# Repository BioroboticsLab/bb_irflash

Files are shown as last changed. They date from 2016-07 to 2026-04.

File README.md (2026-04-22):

# bb_irflash - Infrared LED flashing software and hardware

----
## What is bb_irflash?

bb_irflash is a software and hardware layout package. It contains the circuit and board layout for creating infrared flashing devices.

## Software

The software is C code written and tested for the Arduino Board Duemilanove. However, it should be easily adjusted to fit any arduino available on the market.

## Hardware

The hardware is designed to be triggered via signal current and powered with 12V. The design contains no protection mechanism whatsoever. So exchanging the resistors and/or LED's enables faster/slower flashing or constant lighting. 

The board dimensions are 23mmx51mm, single sided layout. Parts as described in the 'Parts' section enable flashing at 3 Hz and 20 ms duration. Designs come in EAGLE format.

# Parts

## SMD Parts Required for the Boards

The following Surface-Mount Device (SMD) parts are required for the boards:

### MOSFETs
- 8x [NTMS4807NR2G 'AO4752'](https://www.mouser.de/ProductDetail/863-NTMS4807NR2G)

### LEDs
- 8x [LED OSRAM 'SFH 4716AS A01'](https://www.mouser.de/ProductDetail/ams-OSRAM/SFH-4716AS-A01?qs=%252BEew9%252B0nqrDXvNyoSKrong%3D%3D)

### Signal Amplifiers
- 4x [Signal Amplifier 'LM358LVIDR'](https://www.mouser.de/ProductDetail/595-LM358LVIDR)

### Resistors
- 32x [2 Ohm Resistor '603-RC2512JK-072RL'](https://www.mouser.de/ProductDetail/603-RC2512JK-072RL)
- 16x [10k Ohm Resistor '71-CRCW060310K0JNEAC'](https://www.mouser.de/ProductDetail/71-CRCW060310K0JNEAC)
- 2x [4.7k Ohm Resistor '71-CRCW06034K70JNEAC'](https://www.mouser.de/ProductDetail/71-CRCW06034K70JNEAC)
- 4x [22k Ohm Resistor '71-CRCW060322K0JNEAC'](https://www.mouser.de/ProductDetail/71-CRCW060322K0JNEAC)
- 1x [20k Ohm Resistor 'R0603'](Beta Layout standard part) [20k Resistor on Mouser '71-CRCW060320K0JNEA'](https://www.mouser.de/ProductDetail/71-CRCW060320K0JNEAC)
)
- 1x [100k Ohm Resistor '71-CRCW0603100KFKEAC'](https://www.mouser.de/ProductDetail/71-CRCW0603100KFKEAC)

### Capacitors
- 4x [0.01uF Capacitor '810-C1005X7R1H103KBE'](https://www.mouser.de/ProductDetail/810-C1005X7R1H103KBE)
- 2x [1uF Capacitor '81-GRM155R61C105MA2D'](https://www.mouser.de/ProductDetail/81-GRM155R61C105MA2D)

### Diodes
- 2x [Schottky Diode 'CDBU0230R-HF'](https://www.mouser.de/ProductDetail/750-CDBU0230R-HF)

### Transistors
- 2x [NPN Transistor 'NSVMMBT2222AM3T5G'](https://www.mouser.de/ProductDetail/863-NSVMMBT2222AM3T5)

### Timer
- 2x [Timer 'NE555DR'](https://www.mouser.de/ProductDetail/595-NE555DR)

### Logic Gates
- 1x [Dual AND Gate '74LVC2G08'](https://www.mouser.de/ProductDetail/771-74LVC2G08DP-G)

## Through-hole-technology (THT) required components to solder on

### Capacitors
- 8x [2mF Capacitor '667-EEU-FP1E202B'](https://www.mouser.de/ProductDetail/667-EEU-FP1E202B)

### MOSFET
- 1x [STD12NF06L-1 'STD12NF06L-1'](https://www.mouser.de/ProductDetail/511-STD12NF06L-1)

### Connectors
- 8x [Header - Board to LED connections](https://www.mouser.de/ProductDetail/538-43045-0400)
- 1x [Header - Arduino connection](https://www.mouser.de/ProductDetail/538-105313-1203).  Note that the picture shows the incorrect part with number 1103.  The right angle connection
- 1x [Header - Power supply connection](https://www.mouser.de/ProductDetail/538-76825-0002)

See order_examples for further detail, and reference the picture for needed parts.  

# Mouser project order templates for parts:
- [bb_irflash SMD components Mouser project to order](https://eu.mouser.com/ProjectManager/ProjectDetail.aspx?AccessID=517e59b65d)
- [bb_irflash SMD components spreadsheet list](order_examples/BB_IRFLASH_SMD_COMPONENTS.xls)
- [bb_irflash THT components Mouser project to order](https://eu.mouser.com/ProjectManager/ProjectDetail.aspx?AccessID=0B309C354D)
- [bb_irflash THT components spreadsheet list](order_examples/BB_IRFLASH_THT_COMPONENTS.xls)
- [Cables for connecting lights, Arduino, and power supply](https://www.mouser.de/ProjectManager/ProjectDetail.aspx?AccessID=e691302b18). Note that the Arduino connection cable (Nanofit) and the power supply cable (Megafit) connect to the board, but will have to be cut/adjusted to make appropriate connections to the Arduino/power supply

# Power supply
The board is typically driven at 5V.  However, higher light output can be achieved by driving at slightly higher voltages.  here are suitable power supply for these voltages.  Note that when operating at 6fps and 5msec flashes, one board will draw 1-1.5 amps maximum.  Therefore one of these power supplies is sufficient to drive multiple boards.
- [5V power supply (adjustable in range 4.75-5.8V)](https://www.mouser.de/ProductDetail/MEAN-WELL/HRP-100-5?qs=Pc4kzEvJlcQLHIPhYtoJzw%3D%3D)
- [7.5V power supply (adjustable in range 6-9V)](https://www.mouser.de/ProductDetail/MEAN-WELL/RSP-320-7.5?qs=Uzd%2Fwh%252BZzhAvdwoq1II01Q%3D%3D).  Also available at [Conrad](https://www.conrad.de/de/p/mean-well-rsp-320-7-5-schaltnetzteil-7-5-v-dc-40-a-300-w-2249344.html?utm_source=google&utm_medium=cpc&utm_campaign=GB1_Messtechnik+%26+Stromversorgung_Generic&utm_id=43483581&gad_source=1&gbraid=0AAAAAD1-3H5RXiWIoMa0wxSd_K8oRlJKH&gclid=CjwKCAiAudG5BhAREiwAWMlSjDPmVMJK24BTLvHd9yjfUtIwc8q5r0EybappmSUyCZYAYHu7tNM5choC1wwQAvD_BwE&refresh=true)

# Board V2.0

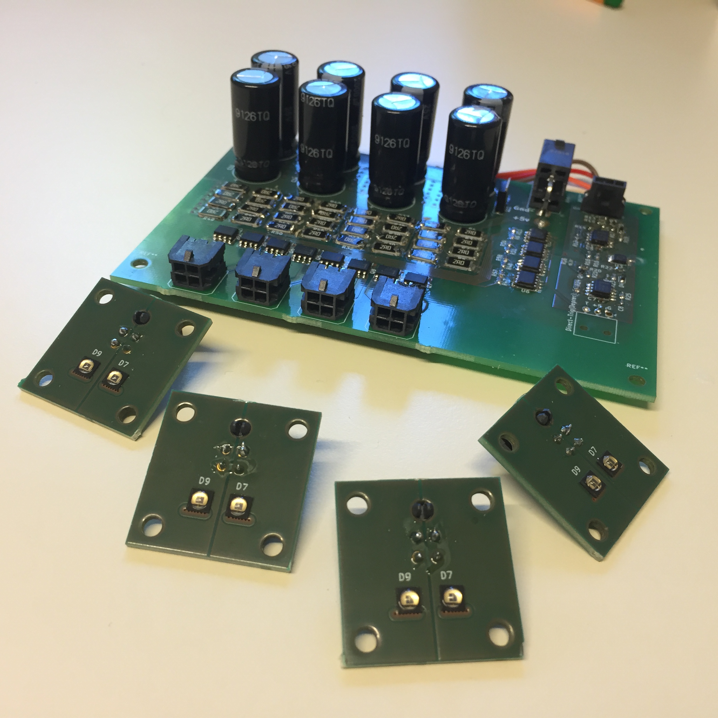
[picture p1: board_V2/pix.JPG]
BoardV2


The new IR flash board have the exact same performance as the previous version. The only new part is a better connectivity and a protection circuit.
The protection circuit is limiting the impulse duration to 20ms with a pause of 100ms between each pulse for protecting the LED. The power supply should be 
V ; 6A. To use it just send a step signal of the wanted duration to the trigger pin of the board (The step signal should not be wider than 20ms high and a pause of 100ms should be observe between each pulse)

The files in "board_V2" folder are all the project file in KiCAD format. If you have no interest in redesign, they are not interesting for you. 

For fabrication you only need the files in the fabrication folder.
The gerber files contained in "fabrication/gerber" are the map of your circuits - You manufacturer would ask for them (likely as a zip file, i.e. gerber.zip containing all folder contents).  The subfolder : "fabrication/gerber/drill_file" contain the coordinate of all the holes drilled into the board.

If you want to ask a third party for assembly, you will need the gerber files, the components position files ("Bestückungsplan": assembly_map_top.pdf
and assembly_map_bottom.pdf), the Pick&Place placement file (Pick&Place.txt), and the components list (Bill of Materials: BOM.xlsx). The 
The components position files are in component_position folder (Bottom and top layer). Note that the BOM format can vary in function of your third party company.

The folder order_examples contains two examples for orders placed through Beta Layout with components ordered through Mouser.  These are for reference.

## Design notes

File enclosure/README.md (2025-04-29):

# Case for Board v2

**Dimensions**:
- Top: 127 x 90 x 31mm
- Bottom: 127 x 90 x 17mm

**Material used:** Black PLA
**Nozzle Size:** 0.4 mm

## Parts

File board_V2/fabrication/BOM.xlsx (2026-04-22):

BILL OF MATERIALS | GROUPED BY VALUES | AS OF 03.14.2024
Part | Value | Device | Package | Description | Description2 | Qty | Place_YES/NO | Provided_by_customer_YES/NO | Distributor | ItemNumber | Remarks
C1, C6, C7, C4, | 0.01u | C | Capacitor_SMD:C_0402_1005Metric | Unpolarized capacitor | Multilayer Ceramic Capacitors MLCC - SMD/SMT SOFT 0402 50V 0.01uF X7R 10% T: 0.5mm | 4 | Y | N | Mouser | 810-C1005X7R1H103KBE | https://www.mouser.fr/ProductDetail/810-C1005X7R1H103KBE
C2, C3, C10, C9, C14, C12, C13, C11, | 2m | CP | Capacitor_THT:CP_Radial_D12.5mm_P5.00mm | Polarized capacitor | Aluminium Electrolytic Capacitors - Radial Leaded 25VDC 2000uF 20% ESR 0.030ohm | 8 | N | N | Mouser | 667-EEU-FP1E202B | https://www.mouser.fr/ProductDetail/667-EEU-FP1E202B
C5, C8, | 1u | C | Capacitor_SMD:C_0402_1005Metric | Unpolarized capacitor | Multilayer Ceramic Capacitors MLCC - SMD/SMT 0402 1uF 16volts X5R 20% | 2 | Y | N | Mouser | 81-GRM155R61C105MA2D | https://www.mouser.fr/ProductDetail/81-GRM155R61C105MA2D
D2, D1, D5, D6, D8, D10, D7, D9, | LED | LED | LED:SFH 4716AS A01 | Light emitting diode | Infrared Emitters - High Power Infrared 850 nm | 8 | Y | N | Mouser | 720-SFH4716ASAA5051 | https://www.mouser.de/ProductDetail/ams-OSRAM/SFH-4716AS-A01?qs=%252BEew9%252B0nqrDXvNyoSKrong%3D%3D
D3, D4, | CDBU0230R-HF | CDBU0230R-HF | Diode_SMD:D_0603_1608Metric | Diode | Schottky Diodes & Rectifiers VR=30V, IO=200mA | 2 | Y | N | Mouser | 750-CDBU0230R-HF | https://www.mouser.fr/ProductDetail/750-CDBU0230R-HF
Q2, Q1, Q5, Q6, Q8, Q10, Q7, Q9, | NTMS4807NR2G | AO4752 | Package_SO:SOIC-8_3.9x4.9mm_P1.27mm |  |  | 8 | Y | N | Mouser | 863-NTMS4807NR2G | https://www.mouser.fr/ProductDetail/863-NTMS4807NR2G
Q3, Q4, | NSVMMBT2222AM3T5G | Q_NPN_BCE | Package_TO_SOT_SMD:SOT-723 | NPN transistor, base/collector/emitter | Bipolar Transistors - BJT SS SOT-723 GP TRANSISTOR | 2 | Y | N | Mouser | 863-NSVMMBT2222AM3T5 | https://www.mouser.fr/ProductDetail/863-NSVMMBT2222AM3T5
Q11, | STD12NF06L-1 | STD12NF06L-1 | Package_TO_SOT_THT:TO-251-3_Vertical | 50V Vds, 0.22A Id, N-Channel MOSFET, SOT-23 | MOSFET TO-251AA N-Ch Power | 1 | N | N | Mouser | 511-STD12NF06L-1 | https://www.mouser.de/ProductDetail/511-STD12NF06L-1 (https://www.mouser.fr/ProductDetail/512-RFD14N05L)
R3, R4, R10, R9, R8, R2, R7, R5, R32, R27, R33, R34, R35, R30, R29, R28, R50, R40, R52, R54, R56, R46, R44, R42, R49, R39, R51, R53, R55, R45, R43, R41, | 2 | R | Resistor_SMD:R_2512_6332Metric | Resistor | Thick Film Resistors - SMD 2 OHM 5% | 32 | Y | N | Mouser | 603-RC2512JK-072RL | https://www.mouser.fr/ProductDetail/603-RC2512JK-072RL
R13, R12, R18, R16, R21, R22, R11, R6, R31, R36, R48, R58, R47, R57, R26, R1, | 10k | R | Resistor_SMD:R_0603_1608Metric | Resistor | Thick Film Resistors - SMD 1/10Watt 10Kohms 5% Commercial Use | 16 | Y | N | Mouser | 71-CRCW060310K0JNEAC | https://www.mouser.fr/ProductDetail/71-CRCW060310K0JNEAC
R15, R20, | 4.7k | R | Resistor_SMD:R_0603_1608Metric | Resistor | Thick Film Resistors - SMD 1/10Watt 4.7Kohms 5% Commercial Use | 2 | Y | N | Mouser | 71-CRCW06034K70JNEAC | https://www.mouser.fr/ProductDetail/71-CRCW06034K70JNEAC
R17, R14, R23, R24, | 22k | R | Resistor_SMD:R_0603_1608Metric | Resistor | Thick Film Resistors - SMD 1/10Watt 22Kohms 5% Commercial Use | 4 | Y | N | Mouser | 71-CRCW060322K0JNEAC | https://www.mouser.fr/ProductDetail/71-CRCW060322K0JNEAC
R19, | 20k | R0603 | Resistor_SMD:R_0603_1608Metric | Resistor |  | 1 | Y | N | Beta | R0603
R25, | 100k | R | Resistor_SMD:R_0603_1608Metric | Resistor | Thick Film Resistors - SMD 1/10Watt 100Kohms 1% Commercial Use | 1 | Y | N | Mouser | 71-CRCW0603100KFKEAC | https://www.mouser.fr/ProductDetail/71-CRCW0603100KFKEAC
U1, U5, U7, U6, | LMV358 | LMV358 | Package_SO:SOIC-8_3.9x4.9mm_P1.27mm | Dual Low-Voltage Rail-to-Rail Output Operational Amplifiers, SOIC-8/SSOP-8 | Operational Amplifiers - Op Amps Low Cost RRO amp General Purpose Dual | 4 | Y | N | Mouser | 595-LM358LVIDR | https://www.mouser.de/ProductDetail/Texas-Instruments/LM358LVIDR?qs=qSfuJ%252Bfl%2Fd53U%2FPkf9lZVw%3D%3D
U2, U4, | NE555DR | LM555 | Package_SO:SOIC-8_3.9x4.9mm_P1.27mm | Timer, DIP-8/SOIC-8/SSOP-8 | Timers & Support Products Precision | 2 | Y | N | Mouser | 595-NE555DR | https://www.mouser.fr/ProductDetail/595-NE555DR
U3, | 74LVC2G08 | 74LVC2G08 | Package_SO:TSSOP-8_3x3mm_P0.65mm | Dual AND Gate, Low-Voltage CMOS |  | 1 | Y | N | Mouser | 771-74LVC2G08DP-G | https://www.mouser.fr/ProductDetail/771-74LVC2G08DP-G

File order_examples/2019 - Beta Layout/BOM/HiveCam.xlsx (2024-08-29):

Source: | /media/huisse/Storage/Shared/HiveCamFinish/HiveCam.sch
Date: | Do 08 Aug 2019 11:50:28 CEST
Tool: | Eeschema 5.1.3-ffb9f22~84~ubuntu18.04.1
Generator: | /usr/share/kicad/plugins/bom_csv_grouped_by_value_with_fp.py
Component Count: | 98
Ref | Qnty | Value | Cmp name | Footprint | Description | Place_YES/NO | Povided_by_customer_YES/NO | Distributor | Remark
C1, C6, C7, C4, | 4 | 0.01u | C | Capacitor_SMD:C_0402_1005Metric | Unpolarized capacitor | Y | Y
C2, C3, C10, C9, C14, C12, C13, C11, | 8 | 2m | CP | Capacitor_THT:CP_Radial_D12.5mm_P5.00mm | Polarized capacitor | N | N |  | We will assemble them ourself
C5, C8, | 2 | 1u | C | Capacitor_SMD:C_0402_1005Metric | Unpolarized capacitor | Y | Y
D2, D1, D5, D6, D8, D10, D7, D9, | 8 | LED | LED | LED:SFH-4716S | Light emitting diode | Y | Y
D3, D4, | 2 | DIODE | DIODE | Diode_SMD:D_0603_1608Metric | Diode symbol for simulation only. Pin order incompatible with official kicad footprints | Y | Y
Q2, Q1, Q5, Q6, Q8, Q10, Q7, Q9, | 8 | NTMS4807NR2G | AO4752 | Package_SO:SOIC-8_3.9x4.9mm_P1.27mm |  | Y | Y
Q3, Q4, | 2 | NSVMMBT2222AM3T5G | Q_NPN_BCE | Package_TO_SOT_SMD:SOT-723 | NPN transistor, base/collector/emitter | Y | Y
Q11, | 1 | RFD14N05L | RFD14N05L | Package_TO_SOT_THT:TO-251-3_Vertical | 50V Vds, 0.22A Id, N-Channel MOSFET, SOT-23 | N | N
R3, R4, R10, R9, R8, R2, R7, R5, R32, R27, R33, R34, R35, R30, R29, R28, R50, R40, R52, R54, R56, R46, R44, R42, R49, R39, R51, R53, R55, R45, R43, R41, | 32 | 2 | R | Resistor_SMD:R_2512_6332Metric | Resistor | Y | Y
R13, R12, R18, R16, R21, R22, R11, R6, R31, R36, R48, R58, R47, R57, R26, R1, | 16 | 10k | R | Resistor_SMD:R_0603_1608Metric | Resistor | Y | Y
R15, R20, | 2 | 4.7k | R | Resistor_SMD:R_0603_1608Metric | Resistor | Y | Y
R17, R14, R23, R24, | 4 | 22k | R | Resistor_SMD:R_0603_1608Metric | Resistor | Y | Y
R19, | 1 | 20k | R | Resistor_SMD:R_0603_1608Metric | Resistor | Y | N | Beta | I saw you have this in stock
R25, | 1 | 100k | R | Resistor_SMD:R_0603_1608Metric | Resistor | Y | Y
U1, U5, U7, U6, | 4 | LMV358 | LMV358 | Package_SO:SOIC-8_3.9x4.9mm_P1.27mm | Dual Low-Voltage Rail-to-Rail Output Operational Amplifiers, SOIC-8/SSOP-8 | Y | Y
U2, U4, | 2 | NE555DR | LM555 | Package_SO:SOIC-8_3.9x4.9mm_P1.27mm | Timer, DIP-8/SOIC-8/SSOP-8 | Y | Y
U3, | 1 | 74LVC2G08 | 74LVC2G08 | Package_SO:TSSOP-8_3x3mm_P0.65mm | Dual AND Gate, Low-Voltage CMOS | Y | Y
Ref | Qnty | Value
C1, C6, C7, C4, | 35 | 0.01u
C2, C3, C10, C9, C14, C12, C13, C11, |  | 2m
C5, C8, | 56 | 1u
D2, D1, D5, D6, D8, D10, D7, D9, | 92 | LED
D3, D4, | 37 | DIODE
Q2, Q1, Q5, Q6, Q8, Q10, Q7, Q9, | 111 | NTMS4807NR2G
Q3, Q4, | 38 | NSVMMBT2222AM3T5G
Q11, |  | RFD14N05L
R3, R4, R10, R9, R8, R2, R7, R5, R32, R27, R33, R34, R35, R30, R29, R28, R50, R40, R52, R54, R56, R46, R44, R42, R49, R39, R51, R53, R55, R45, R43, R41, | 364 | 2
R13, R12, R18, R16, R21, R22, R11, R6, R31, R36, R48, R58, R47, R57, R26, R1, | 240 | 10k
R15, R20, | 35 | 4.7k
R17, R14, R23, R24, | 66 | 22k
R19, |  | 20k
R25, | 38 | 100k
U1, U5, U7, U6, | 56 | LMV358
U2, U4, | 38 | NE555DR
U3, | 19 | 74LVC2G08

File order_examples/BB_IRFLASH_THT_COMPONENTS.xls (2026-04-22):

BB_IRFLASH THT COMPONENTS
Mouser-Nr. | Herst.- Nr. | Hersteller | Kunden-Teilenr | Beschreibung | RoHS | Lebenszyklus | Stückzahl
538-105313-1203 | 105313-1203 | Molex | J2 | Sockel & Kabelgehäuse NanoFit RA Hdr TH SR 3Ckt 0.38UM Au Blk | RoHS-konform |  | 1
511-STD12NF06L-1 | STD12NF06L-1 | STMicroelectronics | Q11 | MOSFETs N-Ch 60V 12A | RoHS: Konform durch Ausnahmegenehmigung |  | 1
538-43045-0400 | 43045-0400 | Molex | J3, J4, J5, J6, J7, J8, J9, J10 | Sockel & Kabelgehäuse 4 CKT R/A HEADER | RoHS-konform |  | 8
538-76825-0002 | 76825-0002 | Molex | J1 | Sockel & Kabelgehäuse MegaFit Dual Row RA Header Tin 2Ckt | RoHS-konform |  | 1
667-EEU-FP1E202B | EEU-FP1E202B | Panasonic | C2, C3, C9, C10, C11, C12, C13, C14 | Aluminium-Elektrolyt-Kondensatoren - Radial bedrahtet 25VDC 2000uF 20% ESR 0.030ohm AECQ200 | RoHS-konform |  | 8

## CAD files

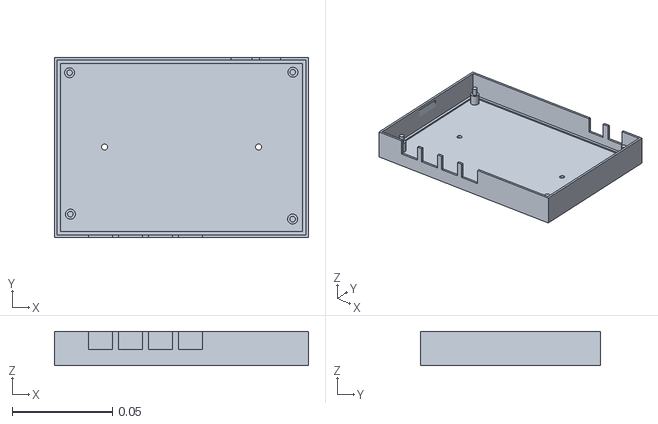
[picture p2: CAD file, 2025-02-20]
enclosure/enclosure_pcb_bottom_v2_20-02.2025.stl
0.127 x 0.09 x 0.017

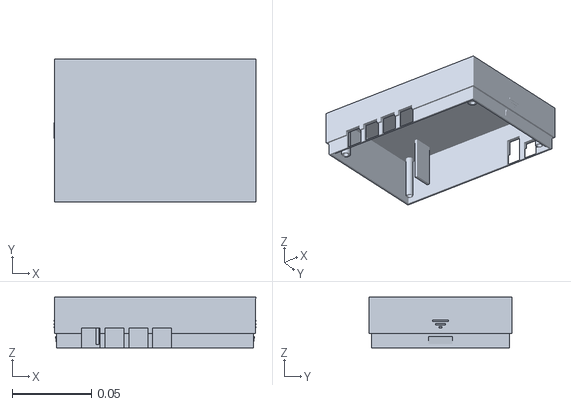
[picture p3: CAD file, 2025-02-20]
enclosure/enclosure_pcb_top_v2_20-02.2025.stl
0.127 x 0.09 x 0.032

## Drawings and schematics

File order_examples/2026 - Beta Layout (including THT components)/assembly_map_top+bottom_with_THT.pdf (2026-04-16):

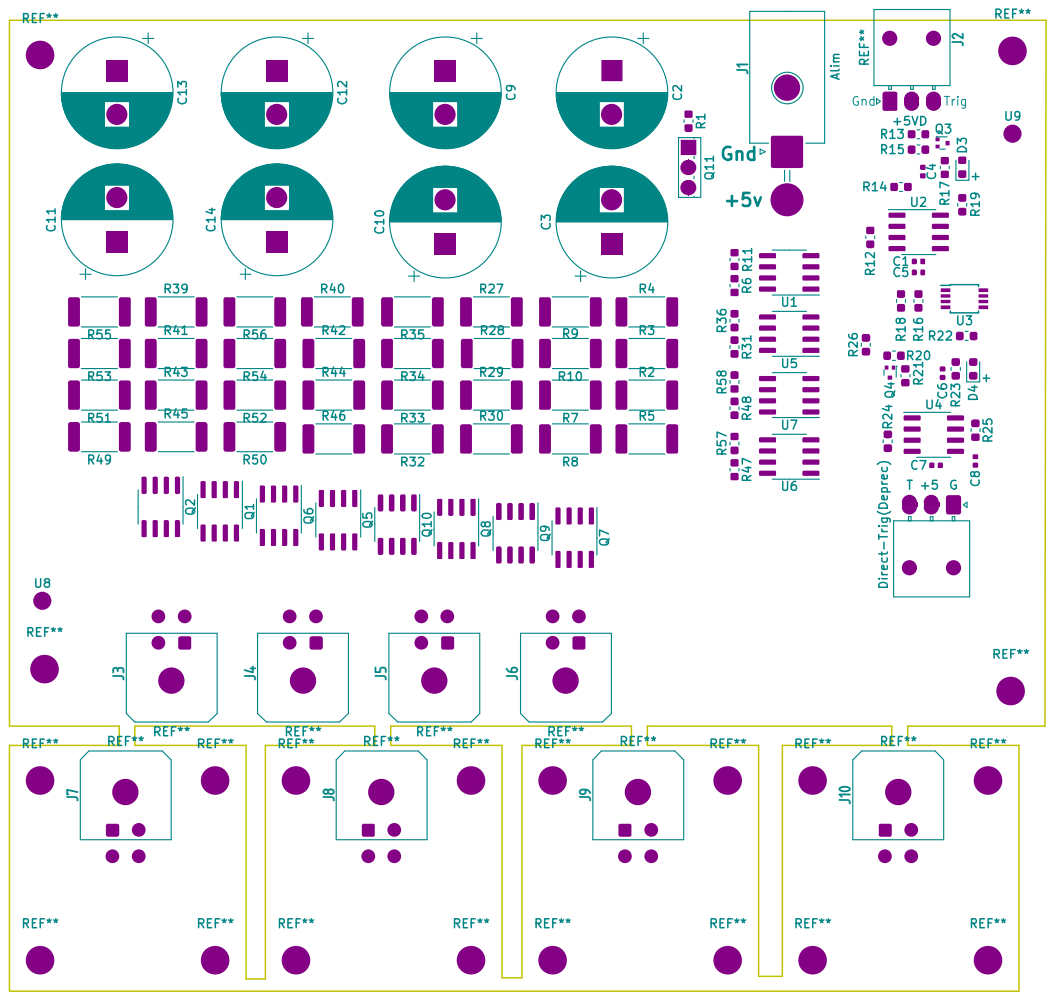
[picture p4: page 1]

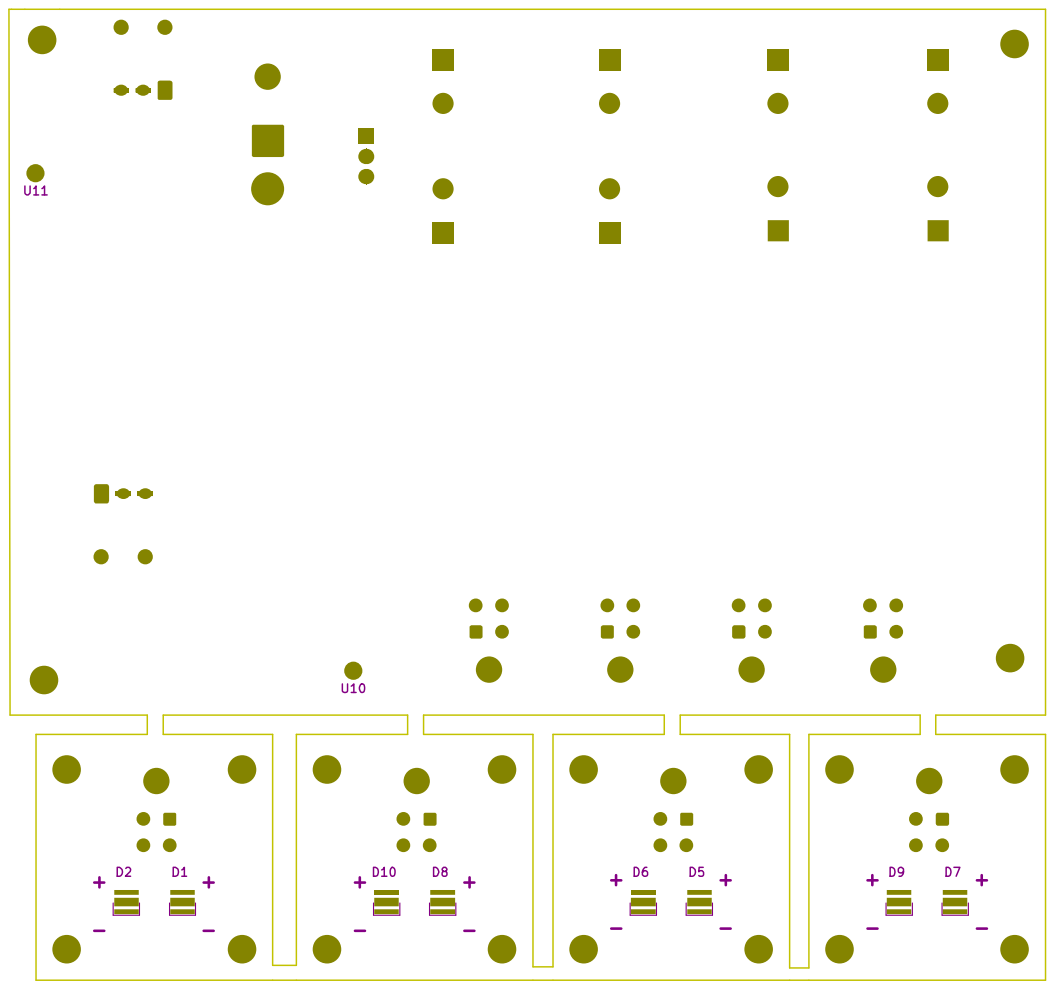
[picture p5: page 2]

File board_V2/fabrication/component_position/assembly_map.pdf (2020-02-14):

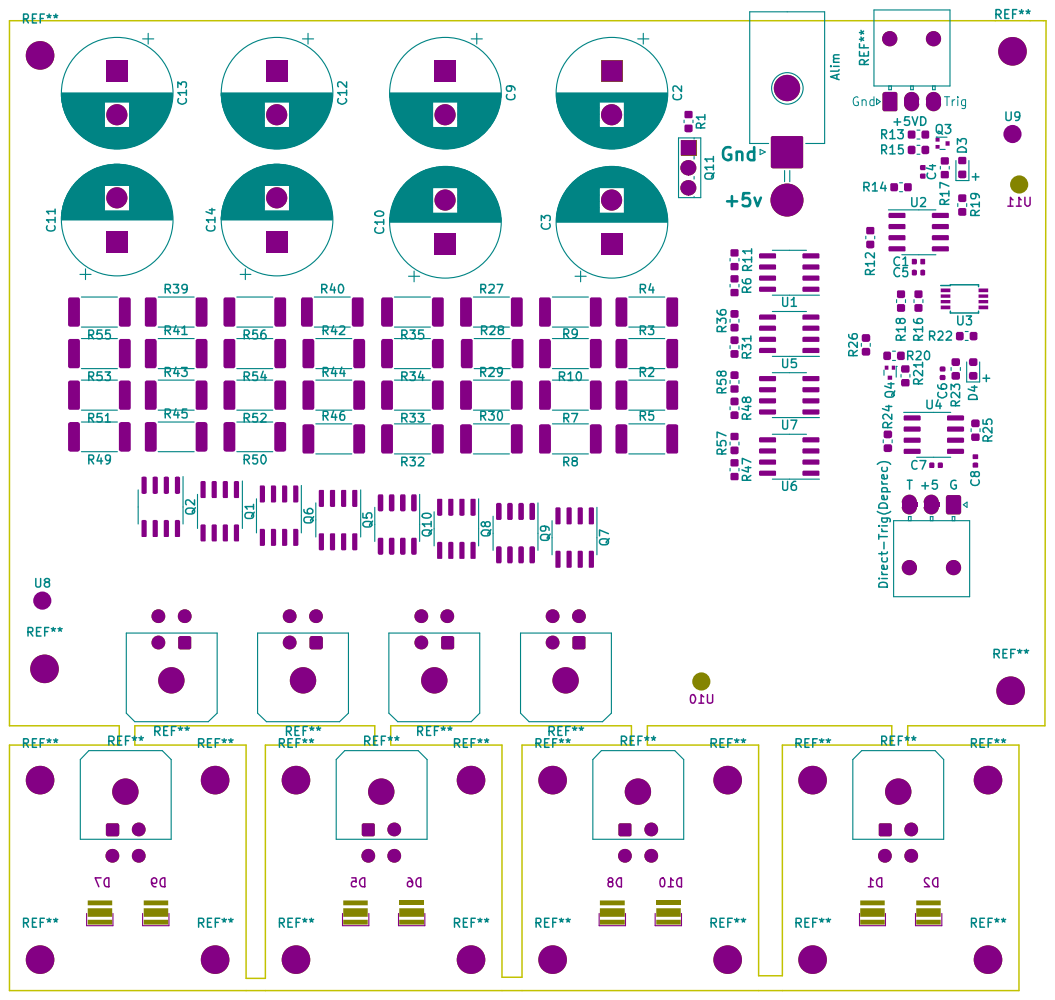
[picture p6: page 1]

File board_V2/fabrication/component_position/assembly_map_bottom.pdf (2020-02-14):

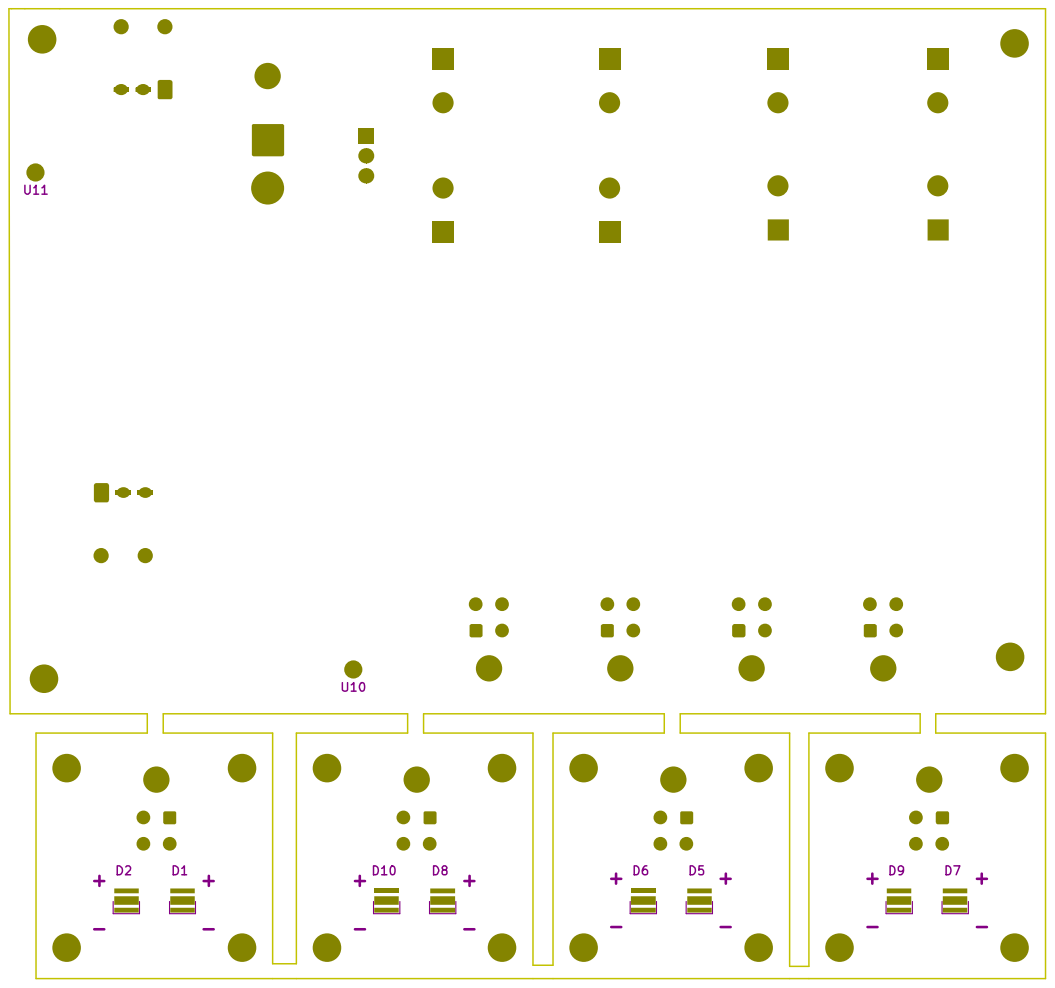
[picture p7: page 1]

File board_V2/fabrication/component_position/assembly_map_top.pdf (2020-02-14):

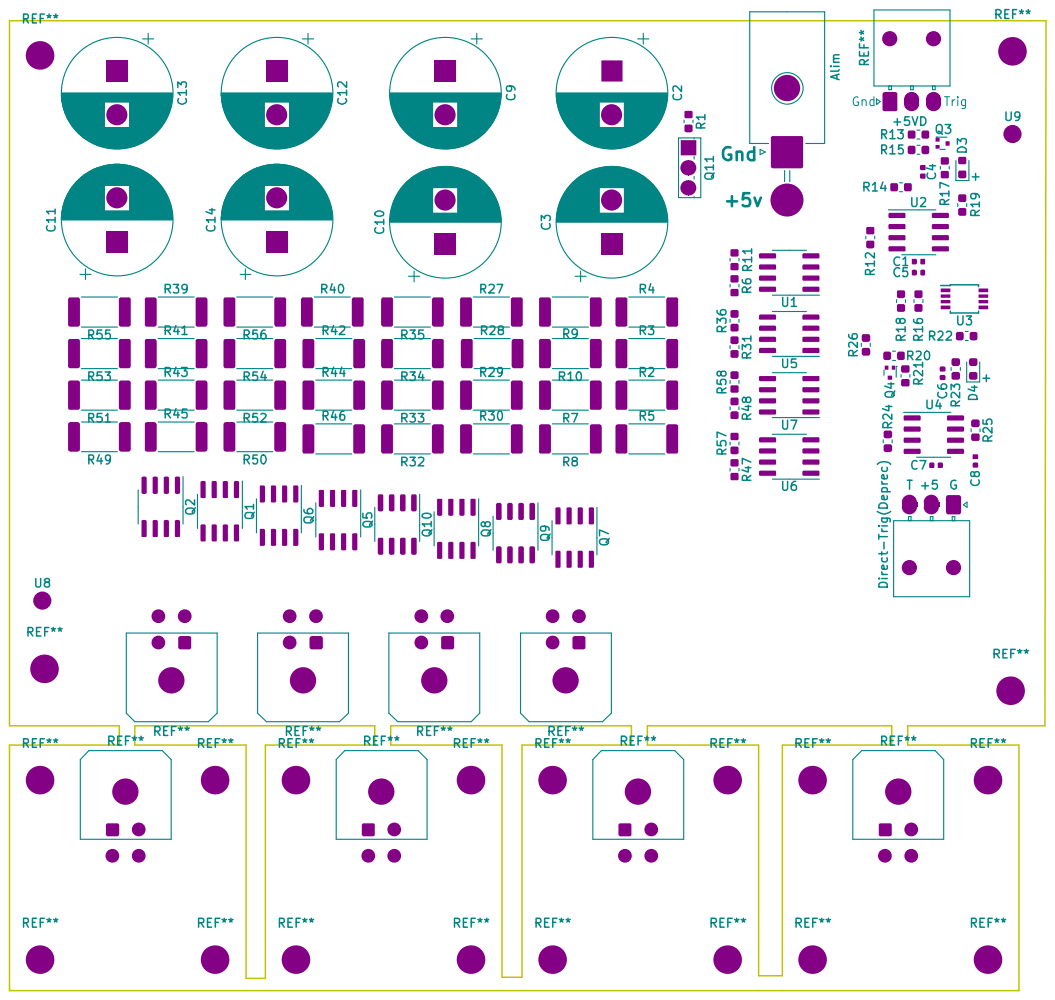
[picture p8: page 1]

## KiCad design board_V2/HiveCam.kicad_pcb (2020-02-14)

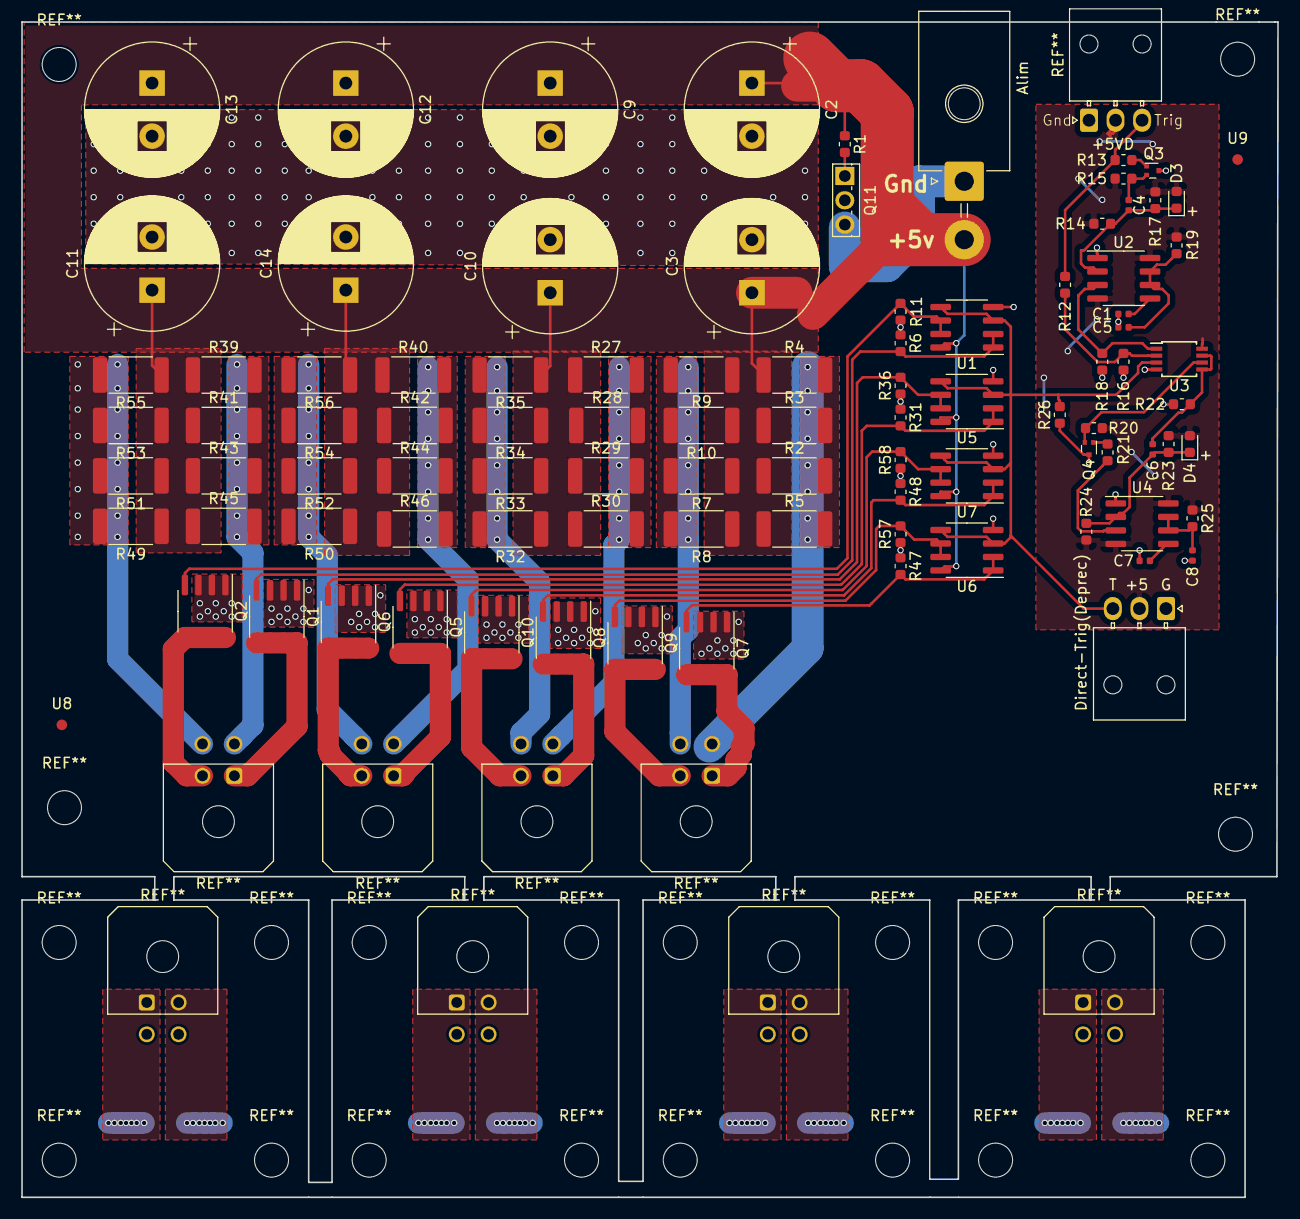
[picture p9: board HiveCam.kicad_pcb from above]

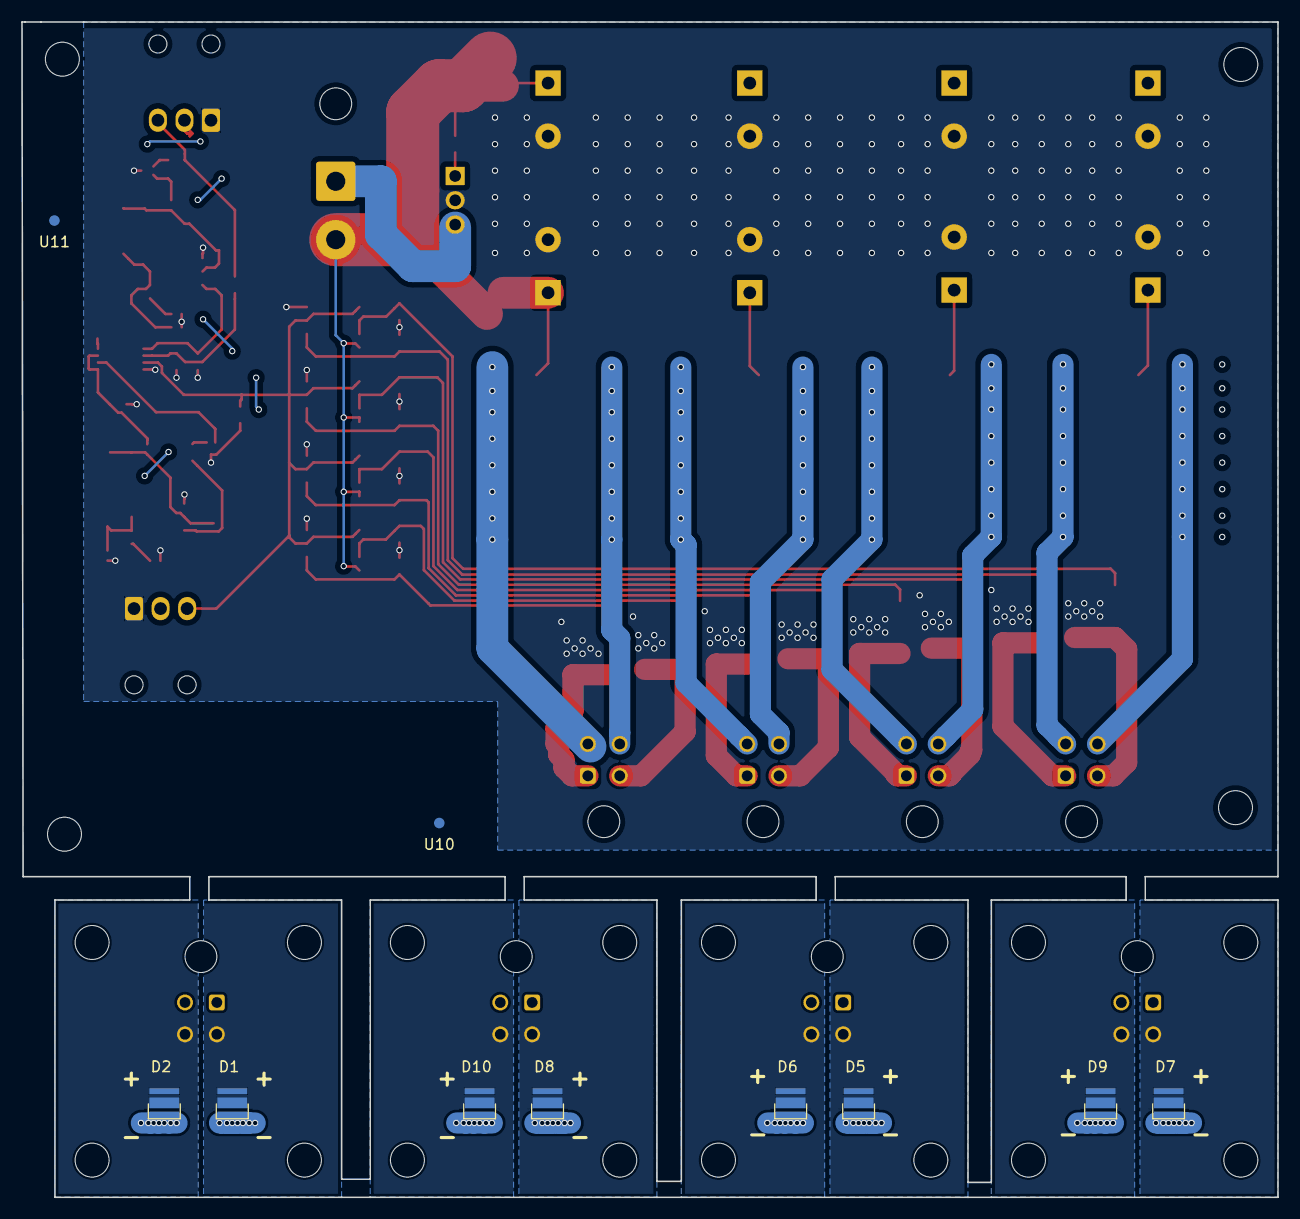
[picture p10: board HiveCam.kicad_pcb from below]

Board: 2 copper layers, 118.3 x 110.7 mm, 104 parts (10 on the bottom side), 39 nets.

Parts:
Alim: Molex_Mega-Fit_76825-0002_2x01_P5.70mm_Horizontal
C1, C4, C6, C7: 0.01u; C_0402_1005Metric
C2, C3, C9, C10, C11, C12, C13, C14: 2m; CP_Radial_D12.5mm_P5.00mm
C5, C8: 1u; C_0402_1005Metric
D1, D2, D5, D6, D7, D8, D9, D10: LED; SFH-4716S
D3, D4: DIODE; D_0603_1608Metric
Direct-Trig(Deprec): Molex_Nano-Fit_105313-xx03_1x03_P2.50mm_Horizontal
Q1, Q2, Q5, Q6, Q7, Q8, Q9, Q10: NTMS4807NR2G; SOIC-8_3.9x4.9mm_P1.27mm
Q3, Q4: NSVMMBT2222AM3T5G; SOT-723
Q11: RFD14N05L; TO-251-3_Vertical
R1, R6, R11, R12, R13, R16, R18, R21, R22, R26, R31, R36, R47, R48, R57, R58: 10k; R_0603_1608Metric
R2, R3, R4, R5, R7, R8, R9, R10, R27, R28, R29, R30, R32, R33, R34, R35, R39, R40, R41, R42, R43, R44, R45, R46, R49, R50, R51, R52, R53, R54, R55, R56: 2; R_2512_6332Metric
R14, R17, R23, R24: 22k; R_0603_1608Metric
R15, R20: 4.7k; R_0603_1608Metric
R19: 20k; R_0603_1608Metric
R25: 100k; R_0603_1608Metric
U1, U5, U6, U7: LMV358; SOIC-8_3.9x4.9mm_P1.27mm
U2, U4: NE555DR; SOIC-8_3.9x4.9mm_P1.27mm
U3: 74LVC2G08; TSSOP-8_3x3mm_P0.65mm
U8, U9, U10, U11: ref; Fiducial_1mm_Mask2mm

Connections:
+5V: Alim.2, C2.1, C3.1, C9.1, C10.1, C11.1, C12.1, C13.1, C14.1, R1.1, R2.1, R3.1, R4.1, R5.1, R7.1, R8.1, R9.1, R10.1, R27.1, R28.1, R29.1, R30.1, R32.1, R33.1, R34.1, R35.1, R39.1, R40.1, R41.1, R42.1, R43.1, R44.1, R45.1, R46.1, R49.1, R50.1, R51.1, R52.1, R53.1, R54.1, R55.1, R56.1, U1.8, U5.8, U6.8, U7.8
+5vD: D3.2, D4.2, Direct-Trig(Deprec).2, R14.2, R15.1, R17.1, R19.1, R20.1, R23.1, R24.2, R25.1, U2.4, U2.8, U3.8, U4.4, U4.8
GND: Alim.1, Q11.3
GNDP: C1.2, C2.2, C3.2, C5.2, C7.2, C8.2, C9.2, C10.2, C11.2, C12.2, C13.2, C14.2, Direct-Trig(Deprec).1, Q1.1, Q1.2, Q1.3, Q2.1, Q2.2, Q2.3, Q3.3, Q4.3, Q5.1, Q5.2, Q5.3, Q6.1, Q6.2, Q6.3, Q7.1, Q7.2, Q7.3, Q8.1, Q8.2, Q8.3, Q9.1, Q9.2, Q9.3, Q10.1, Q10.2, Q10.3, Q11.2, R6.1, R11.1, R16.1, R18.1, R22.1, R26.1, R31.1, R36.1, R47.1, R48.1, R57.1, R58.1, U1.4, U2.1, U3.4, U4.1, U5.4, U6.4, U7.4
unnamed: C1.1, U2.5
unnamed: C4.1, D3.1, R14.1, R17.2, U2.2
unnamed: C4.2, Q3.2, R15.2
unnamed: C5.1, R19.2, U2.6, U2.7
unnamed: C6.1, D4.1, R23.2, R24.1, U4.2
unnamed: C6.2, R22.2, U3.5, U3.7
unnamed: C7.1, U4.5
unnamed: C8.1, R25.2, U4.6, U4.7
unnamed: R2.2, R3.2, R4.2, R5.2
unnamed: R7.2, R8.2, R9.2, R10.2
unnamed: R27.2, R28.2, R29.2, R30.2
unnamed: R32.2, R33.2, R34.2, R35.2
unnamed: D1.1, D5.1, D7.1, D8.1, Q7.5
unnamed: D1.2, D5.2, D7.2, D8.2, R39.2, R41.2, R43.2, R45.2
unnamed: R40.2, R42.2, R44.2, R46.2
unnamed: D2.1, D6.1, D9.1, D10.1, Q9.5
unnamed: D2.2, D6.2, D9.2, D10.2, R49.2, R51.2, R53.2, R55.2
unnamed: R50.2, R52.2, R54.2, R56.2
unnamed: Q1.4, R6.2, U1.1, U1.2
unnamed: Q2.4, R11.2, U1.6, U1.7
unnamed: Q3.1, R13.1
unnamed: Q4.1, R21.1
unnamed: Q4.2, R20.2, U3.6
unnamed: Q5.4, R31.2, U5.1, U5.2
unnamed: Q6.4, R36.2, U5.6, U5.7
unnamed: Q7.4, R47.2, U6.1, U6.2
unnamed: Q8.4, R48.2, U7.1, U7.2
unnamed: Q9.4, R57.2, U6.6, U6.7
unnamed: Q10.4, R58.2, U7.6, U7.7
unnamed: Q11.1, R1.2
unnamed: R12.2, R16.2, U3.2
unnamed: R18.2, U2.3, U3.1
unnamed: R21.2, U4.3
unnamed: Direct-Trig(Deprec).3, R26.2, U1.3, U1.5, U3.3, U5.3, U5.5, U6.3, U6.5, U7.3, U7.5
Trigger: R12.1, R13.2

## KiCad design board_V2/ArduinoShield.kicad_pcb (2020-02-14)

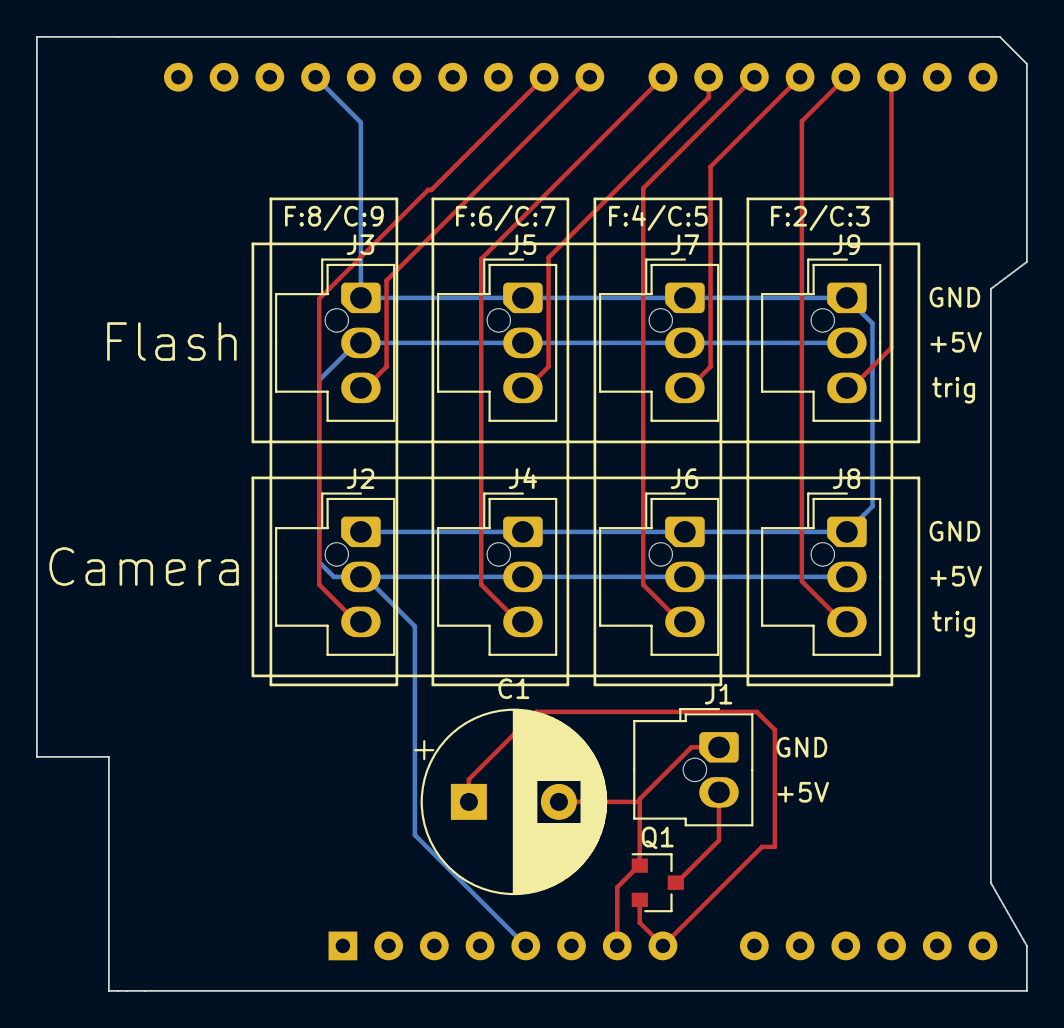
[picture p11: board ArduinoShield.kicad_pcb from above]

Board: 2 copper layers, 55.0 x 53.0 mm, 12 parts (1 on the bottom side), 13 nets.

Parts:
A1: Arduino_UNO_R3
C1: EEU-TP1E511B; CP_Radial_D10.0mm_P5.00mm
J1: Conn_01x02; Molex_Nano-Fit_105309-xx02_1x02_P2.50mm_Vertical
J2, J3, J4, J5, J6, J7, J8, J9: Conn_01x03; Molex_Nano-Fit_105309-xx03_1x03_P2.50mm_Vertical
Q1: NTR1P02T1G; SOT-23

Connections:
unnamed: A1.7, C1.2, J1.1, Q1.1
unnamed: A1.8, C1.1, Q1.2
unnamed: A1.17, J9.3
unnamed: A1.18, J8.3
unnamed: A1.19, J7.3
unnamed: A1.20, J6.3
unnamed: A1.21, J5.3
unnamed: A1.22, J4.3
unnamed: A1.23, J3.3
unnamed: A1.24, J2.3
unnamed: A1.29, J2.1, J3.1, J4.1, J5.1, J6.1, J7.1, J8.1, J9.1
unnamed: J1.2, Q1.3
unnamed: A1.5, J2.2, J3.2, J4.2, J5.2, J6.2, J7.2, J8.2, J9.2

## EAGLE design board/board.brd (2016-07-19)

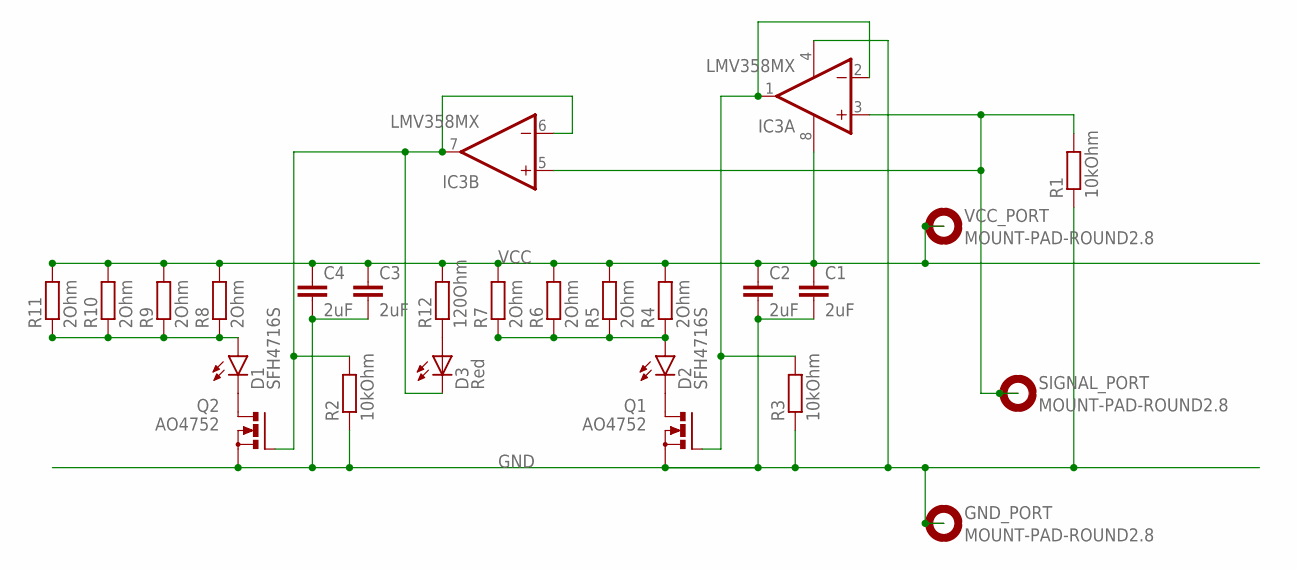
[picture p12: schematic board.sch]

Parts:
C1, C2, C3, C4: 2uF; C0603
D1, D2: SFH4716S; SFH4641
D3: Red; LED5MM
GND_PORT: MOUNT-PAD-ROUND2.8; 2,8-PAD
IC3: LMV358MX; SO08
Q1, Q2: AO4752; SO-08
R1, R2, R3: 10kOhm; R0603
R4, R5, R6, R7, R8, R9, R10, R11: 2Ohm; R2512
R12: 120Ohm; R0603
SIGNAL_PORT: MOUNT-PAD-ROUND2.8; 2,8-PAD
VCC_PORT: MOUNT-PAD-ROUND2.8; 2,8-PAD

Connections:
F1: D2.C, Q1.5 (D), Q1.6 (D), Q1.7 (D), Q1.8 (D)
F2: D1.C, Q2.5 (D), Q2.6 (D), Q2.7 (D), Q2.8 (D)
GND: C1.2, C2.2, C3.2, C4.2, GND_PORT.B2,8, IC3.4 (V-), Q1.1 (S), Q1.2 (S), Q1.3 (S), Q2.1 (S), Q2.2 (S), Q2.3 (S), R1.1, R2.1, R3.1
L1: D1.A, R8.1, R9.1, R10.1, R11.1
L2: D2.A, R4.1, R5.1, R6.1, R7.1
unnamed: D3.A, R12.1
unnamed: D3.K (C), IC3.6 (-IN), IC3.7 (OUT), Q2.4 (G), R2.2
unnamed: IC3.3 (+IN), IC3.5 (+IN), R1.2, SIGNAL_PORT.B2,8
unnamed: IC3.1 (OUT), IC3.2 (-IN), Q1.4 (G), R3.2
VCC: C1.1, C2.1, C3.1, C4.1, IC3.8 (V+), R4.2, R5.2, R6.2, R7.2, R8.2, R9.2, R10.2, R11.2, R12.2, VCC_PORT.B2,8

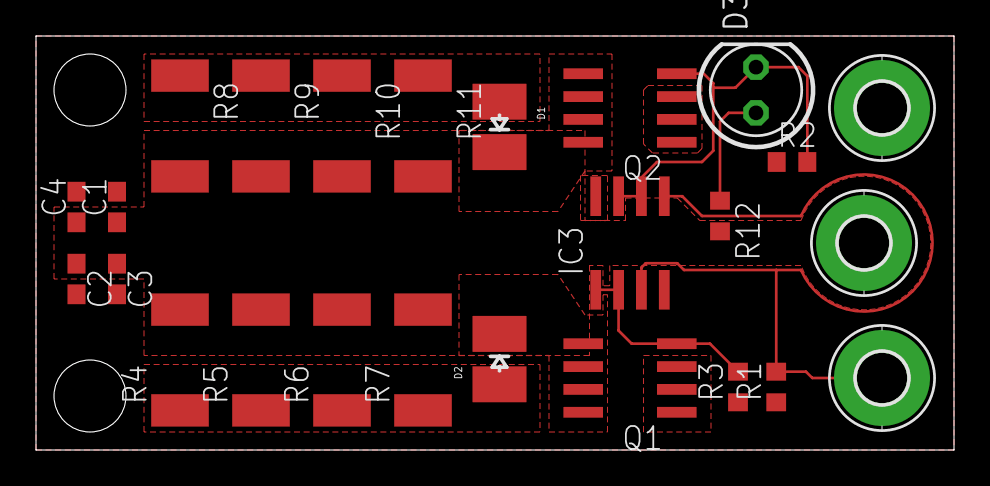
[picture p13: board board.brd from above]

Board: 1 copper layer, 51.0 x 23.0 mm, 25 parts (0 on the bottom side), 10 nets.

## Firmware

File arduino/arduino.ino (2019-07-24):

#include <util/delay.h>

#define CamPinA           3
#define CamPinB           9
#define LEDPinA1          5
#define LEDPinA2          6
#define LEDPinB1          10
#define LEDPinB2          11
#define FPS               6
//Flashing time is flash+camFlashOffset+Trigertime
//Workflow: Flash on -> wait the offset -> trigger cam -> wait triggertime
//          -> untrigger cam -> wait flash -> Flash off 
#define flash             (5.5)
#define second            1000.0

// Needs to be compile-time constant.
// void accurateDelayMicroseconds(float us)
#define accurateDelayMicroseconds(us)\
{\
  noInterrupts();\
  _delay_us(us);\
  interrupts();\
}\

// the setup function runs once when you press reset or power the board
void setup() {
  pinMode(CamPinA, OUTPUT);
  pinMode(CamPinB, OUTPUT);
  pinMode(LEDPinA1, OUTPUT);
  pinMode(LEDPinB1, OUTPUT);
  pinMode(LEDPinA2, OUTPUT);
  pinMode(LEDPinB2, OUTPUT);
}

void triggerDual(int portCam, int portLED, int portLED2){
  // We trigger on rising-edge.
  analogWrite(portCam,255); // Trigger.
  // Trigger flashes. The camera might need a few micros, but the flashes also need to bright up.
  analogWrite(portLED,255);  
  analogWrite(portLED2,255);
  accurateDelayMicroseconds(3.5 * 1000.0);
  // Reset the signals.
  analogWrite(portCam, 0);
  analogWrite(portLED, 0);
  analogWrite(portLED2, 0);
  // Grace period. Potentially unnecessary.
  // Tiny bit less than the configured flash time, because the function calls also have overhead.
  accurateDelayMicroseconds(1.99 * 1000.0);
}

// the loop function runs over and over again forever
void loop() {  
 
  //E.g. we have two fps: flash at 0 cam A, 250 cam B, 500 cam A ...
  const float halfFlash = (1000.0 * second) / static_cast<float>(FPS) / 2.0 - flash * 1000.0;

  int i=0;
  for(i=0 ; i<FPS ; i++){
    //LED for debug
    digitalWrite(13, HIGH);

    //flash camera A and wait half a frame
    triggerDual(CamPinA,LEDPinA1,LEDPinA2); 
    digitalWrite(13, LOW);
    accurateDelayMicroseconds(halfFlash);
    triggerDual(CamPinB,LEDPinB1,LEDPinB2); 
    accurateDelayMicroseconds(halfFlash);
  }
}

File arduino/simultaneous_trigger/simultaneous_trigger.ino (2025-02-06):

#include <util/delay.h>

#define PIN_CAM_A         3
#define PIN_CAM_B         9
#define PIN_LED_A         5
#define PIN_LED_B         6
#define TARGET_FPS        6

#define TRIGGER_MODE_SIMULTANEOUS
// #define TRIGGER_MODE_ALTERNATING

#define LED_LATENCY_US    1000   
#define CAM_EXPOSURE_US   15000       

// Needs to be compile-time constant.
// void accurateDelayMicroseconds(float us)
#define accurateDelayMicroseconds(us)\
{\
  noInterrupts();\
  _delay_us(us);\
  interrupts();\
}\

// the setup function runs once when you press reset or power the board
void setup() {
  pinMode(PIN_CAM_A, OUTPUT);
  pinMode(PIN_CAM_B, OUTPUT);
  pinMode(PIN_LED_A, OUTPUT);
  pinMode(PIN_LED_B, OUTPUT);
}

void triggerSimultaneous()
{
  // switch both LED boards on
  analogWrite(PIN_LED_A, 255);
  analogWrite(PIN_LED_B, 255);

  // wait 1 ms for the LEDs to reach maximum brightness
  accurateDelayMicroseconds(LED_LATENCY_US);
  
  // trigger cameras to record a frame
  analogWrite(PIN_CAM_A, 255);
  analogWrite(PIN_CAM_B, 255);

  // wait 1 ms for the cams before switching off
  accurateDelayMicroseconds(CAM_EXPOSURE_US);
  
  // set cam trigger off
  analogWrite(PIN_CAM_A, 0);
  analogWrite(PIN_CAM_B, 0);

  // switch both LED boards off
  analogWrite(PIN_LED_A, 0);
  analogWrite(PIN_LED_B, 0);
}

void loop() 
{  

  //number of ms defined by the framerate minus the combined waiting times after LED and cam trigger, respectively (in ms)
  const float WAIT_UNTIL_NEXT_FRAME_US = 1000000.0 / TARGET_FPS - (LED_LATENCY_US + CAM_EXPOSURE_US);

  // debug LED on 
  digitalWrite(13, HIGH);
  
  int i=0;
  for(i=0 ; i<TARGET_FPS ; i++)
  {
    // trigger cams and LEDs
    triggerSimultaneous();

    // wait remaining time
    accurateDelayMicroseconds( WAIT_UNTIL_NEXT_FRAME_US );
  }

  // debug LED off 
  digitalWrite(13, LOW);  
}

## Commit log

2019-07-24 increased time between frames a little
2020-02-14 Adding V2 board
    [ArduinoShield.kicad_pcb, ArduinoShield.sch, HiveCam-B_Adhes.gbr, HiveCam-B_CrtYd.gbr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]
2024-03-20 updated part numbers, cleaned up contents, added order examples
    Note: removed 'HiveCam' folder, because its contents were the same as board_v2. Moved PDFs with order details to separate folder, updated component links to Mouser, and included updated bill of mater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
    [ArduinoShield.kicad_pcb, ArduinoShield.sch, BOM.xlsx, HiveCam-B_Adhes.gbr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]
2024-11-12 added xls Mouser component lists
    [BB_IRFLASH_SMD_COMPONENTS.xls, BB_IRFLASH_THT_COMPONENTS.xls]
2025-02-20 Add 3D enclosure model files
    [enclosure_pcb_bottom_v2_20-02.2025.stl, enclosure_pcb_top_v2_20-02.2025.stl, enclosure_pcb_v2_20-02-2025.blend]
2026-04-16 mosfet corrected to tht version
    [BB_IRFLASH_THT_COMPONENTS.xls]
2026-04-16 add order including THT components
    [BOM_v2_with_THT.xlsx]
2026-04-22 replace mosfet due to end-of-life for other part
    [BB_IRFLASH_THT_COMPONENTS.xls, BOM.xlsx, BOM_v2_with_THT.xlsx]

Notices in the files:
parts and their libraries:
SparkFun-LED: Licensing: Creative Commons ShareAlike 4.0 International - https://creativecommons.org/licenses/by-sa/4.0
